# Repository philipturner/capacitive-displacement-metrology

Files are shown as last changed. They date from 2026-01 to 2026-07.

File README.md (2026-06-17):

# Capacitive Displacement Metrology

Phase 0.2/I/II of the [APM Roadmap](https://github.com/philipturner/apm-roadmap)

Objective: Finish a project that has dragged on for 14 months.

Deadline: April 31, 2026 for creepless imaging of graphite

Table of Contents:
- [December 15, 2025](#december-15-2025)
- [December 16, 2025](#december-16-2025)
- [December 18, 2025](#december-18-2025)
- [December 22, 2025](#december-22-2025)
- [January 3, 2026](#january-3-2026)
- [January 5, 2026](#january-5-2026)
- [January 6, 2026](#january-6-2026)
- [January 7, 2026](#january-7-2026)
- [January 8, 2026](#january-8-2026)
- [January 9, 2026](#january-9-2026)
- [January 12, 2026](#january-12-2026)
- [January 13, 2026](#january-13-2026)
- [January 14, 2026](#january-14-2026)
- [January 15, 2026](#january-15-2026)
- [January 16, 2026](#january-16-2026)
- [January 20, 2026](#january-20-2026)
- [January 24, 2026](#january-24-2026)
- [January 26, 2026](#january-26-2026)
- [January 29, 2026](#january-29-2026)
- [January 30, 2026](#january-30-2026)
- [February 2, 2026](#february-2-2026)
- [February 3, 2026](#february-3-2026)
- [February 11, 2026](#february-11-2026)
- [February 12, 2026](#february-12-2026)
- [February 17, 2026](#february-17-2026)
- [February 27, 2026](#february-27-2026)
- [March 8, 2026](#march-8-2026)
- [March 9, 2026](#march-9-2026)
- [March 10, 2026](#march-10-2026)
- [March 12, 2026](#march-12-2026)
- [March 20, 2026](#march-20-2026)
- [March 26, 2026](#march-26-2026)
- [March 28, 2026](#march-28-2026)
- [March 29, 2026](#march-29-2026)
- [April 2, 2026](#april-2-2026)
- [April 27, 2026](#april-27-2026)
- [May 4, 2026](#may-4-2026)
- [Jun 1, 2026](#jun-1-2026)
- [Jun 7, 2026](#jun-7-2026)
- [Jun 17, 2026](#jun-17-2026)

## December 15, 2025

$80,000 worth of wire transfers have hit the bank. I now have enough financial security to proceed with hardware work.

The first step is ensuring I can be paid a full-time salary. Comply with US tax laws, SEC regulations, etc. I predicted the exact numbers before going through the legal boilerplate and setup.

To save effort, serious work <i>probably</i> won't begin until Jan 2 2026. I can avoid filing a few tax return documents for the 2025 year. I will figure out some remaining tax and paperwork stuff during the last days of 2025.

Current estimate for the press release is Dec 18 2025.

## December 16, 2025

This is ridiculous. The United States is the only country where taxes are such a pain: https://www.propublica.org/article/inside-turbotax-20-year-fight-to-stop-americans-from-filing-their-taxes-for-free

## December 18, 2025

I want to make the creepless SPM happen in the shortest amount of time, and publish transparent data that can be fact-checked. To stay true to my motive, I made another attempt to persuade Robert Wolkow to cooperate. I could save many person-hours, recycling existing designs for creepless SPM hardware.

Regardless of whether he shares any design information, I will proceed according to plan. Any data published by other sources should be treated with extreme skepticism. Do not trust any other lab's data, except data gathered in my own house.

| Phase | Description | Voltage |
| ----: | ----------- | ------: |
| 0.2   | PZT metrology | 24&ndash;40 V |
| 1.1   | LiNbO3 metrology | 850 V |
| 1.2   | LiNbO3 kinematic mount | 850 V |
| 2.1   | LiNbO3 STM, graphite sample | 850 V |
| 2.2   | LiNbO3 STM, inverted mode tip registration | 850 V |

I can shortcut to an important milestone, without the expensive vacuum chamber. Just need to speed up the progress with tripod synthesis. No additional employees or contractors needed for hardware design.

At the end of Phase 0.2, we'll reflect on how long this phase took. If it happened quickly, we can reach the end goal with a single employee. Otherwise, I will probably hire a temporary contractor for hardware design. Phase 2.2 should be completed before Dec 31 2026.

> Nomenclature change: exclude Roman numerals from the phase names, at least when numbering sub-phases. It's highly cumbersome to process "I.1" and "II.2", versus "1.1" and "2.2".
>
> In addition, we may right-align the phase names in tables and spreadsheets.

## December 22, 2025

Still figuring out taxes, but making progress. Putting work on the next MNT animation on hold. Not really motivated when the response to the tutorial is anemic.

Figuring out the details of a possible contract with ChimiaDAO. Our funds should last us well beyond 6 months into the future: oversee completion of Phase 0.2, stable income while raising funds for the next round. Progress on the tripod synthesis will be reported in the Phase 0.2 repository, alongside hardware progress.

## January 3, 2026

We are now sufficiently ready to return to experiments. Paid labor will start on January 5. Rippling costs a ridiculous $1,800 sign-on contract over 18 months ($150 down payment). Definitely not what they publicly advertise or what you get from LLM summaries. In the future, we will face similar obfuscation of quotes from hardware suppliers (e.g. UHV-quality turbopumps cost $14,000 minimum).

## January 5, 2026

I will start by resolving an important unknown. How much does it cost to have 500 nm range instead of 80 nm range for the LiNbO3 piezos? This has implications all through Phase III, where we integrate a custom scanner into the vacuum chamber. It explodes the design cost in Phase III because Wolkow will likely be selling his own design. Already designed hardware is cheaper than the person-hours cost of designing new hardware.

https://www.matsusada.com/corporate/management.html

Might contact Matsusada after doing my own research on their products and my performance requirements.

https://www.matsusada.com/column/hvps-safty.html

### Modeling Power Supply Requirements

To be conservative, assume we'll need 3 kinematic mounts for X, Y, and Z. We're also reducing the range, with 6 plates from Wolkow's patent instead of 10. Now all actuators, for all axes, use 6-high piezo stacks. The capacitance of the kinematic mount probably prevents utilization of the PA94 for high slew rates.

Design options for piezo stack geometry:
- 6 plates, 5 mm x 5 mm area, 6 mm stack height
- 6 plates, 10 mm x 10 mm area, 6 mm stack height
- 10 plates, 10 mm x 10 mm area, 10 mm stack height

The plate area is important now, because smaller plates have less capacitance, and thus lower current pulse requirements for the power supply. We may also use different plate areas for the fine vs. coarse actuators. Mechanically, sticking two 5 mm x 5 mm stacks on top of each other would create a 12 mm high tower. Not a good idea.

### Modeling Piezo Force Requirements

To break static friction, the piezo needs to generate a certain amount of force. In addition to the range and waveform frequency requirements.

Assuming a 0.5 mm thick plate and 69.2 GPa shear modulus:

| Voltage | Displacement | Shear Proportion | Shear Pressure |
| ------: | -----------: | ---------------: | -------------: |
| 200 V   | 13.6 nm      | 2.72e-5          | 1.88e6 Pa      |
| 850 V   | 57.8 nm      | 1.16e-4          | 8.00e6 Pa      |

Forces for various setups at 200 V:

| Plate Size | Plate Count | Shear Force | Max Weight |
| ---------- | ----------: | ----------: | ---------: |
| 5 mm x 5 mm   | 1 | 47.1 N | 4.8 kg |
| 5 mm x 5 mm   | 3 | 141.1 N | 14.4 kg |
| 10 mm x 10 mm | 1 | 188.2 N | 19.2 kg |
| 10 mm x 10 mm | 3 | 564.7 N | 57.6 kg |

Forces for various setups at 850 V:

| Plate Size | Plate Count | Shear Force |
| ---------- | ----------: | ----------: |
| 5 mm x 5 mm   | 1 | 200.0 N | 20.4 kg |
| 5 mm x 5 mm   | 3 | 600.0 N | 61.2 kg |
| 10 mm x 10 mm | 1 | 800.0 N | 81.6 kg |
| 10 mm x 10 mm | 3 | 2399.9 N | 244.9 kg |

Even though shear force doesn't increase with the number of plates per stack, the above numbers should exceed all reasonable force requirements.

### Modeling Required Slew Rate

Dive deeper into the waveform requirements for stick-slip nanopositioning:
- Does the waveform need to contain components above the resonance frequency?
- What is the target rate in steps/second?
- Why is woodpecker coarse tip approach so slow?

These variables can probably be resolved at a later date. I mostly want a lower capacitance in the kinematic mount, while still attaining 30 V/μs slew rate of the PA95 op amp.

### Design Space Exploration

Quiescent current demands on power supply:
- Conservatively 6 DAC channels and 6 PA95 op amps for Phase III
- 6 * 2.2 mA = 13.2 mA

Capacitance (in pF) of entire kinematic mount:
- Piezo plate count is 18 (3 stacks, each with 6 plates)
- Dielectric constant of lithium niobate at 300 K is 88
- Thickness of each plate is 0.5 mm

| Configuration | Capacitance |
| ------------- | ----------: |
| 5 mm x 5 mm   | 701         |
| 10 mm x 10 mm | 2805        |

Current (in mA) required to drive the kinematic mount:

| Configuration | 30 V/μs | 20 V/μs | 10 V/μs | 5 V/μs | 3 V/μs |
| ------------- | ------: | ------: | ------: | -----: | -----: |
| 5 mm x 5 mm   | 21.0    | 14.0    | 7.0     | 3.5    | 2.1    |
| 10 mm x 10 mm | 84.2    | 56.1    | 28.1    | 14.0   | 8.4    |

Power (in W) generated by either of the 450 V power supplies:
- Each supply operates at ~50% duty cycle
- Each supply operates during the respective edge of the waveform
  - +450 V for rising
  - -450 V for falling

| Configuration | 30 V/μs | 20 V/μs | 10 V/μs | 5 V/μs | 3 V/μs |
| ------------- | ------: | ------: | ------: | -----: | -----: |
| 5 mm x 5 mm   | 9.5     | 6.3     | 3.2     | 1.6    | 0.9    |
| 10 mm x 10 mm | 37.9    | 25.2    | 12.6    | 6.3    | 3.8    |

Frequency of an 850 V triangle wave:

| Slew rate (V/μs)     | 30   | 20   | 10  | 5   | 3   |
| -------------------- | ---: | ---: | --: | --: | --: |
| Rise time (μs)       | 28   | 43   | 85  | 170 | 283 |
| Wave period (μs)     | 57   | 85   | 170 | 340 | 567 |
| Wave frequency (kHz) | 17.6 | 11.8 | 5.9 | 2.9 | 1.8 |

### Final Current Demands

Making the smart design choice to use 5 mm instead of 10 mm piezo plates for the kinematic mount.

Providing two negotiable options for maximum waveform frequency: 5.9 kHz, 17.6 kHz

| Wave frequency                        | 5.9 kHz  | 17.6 kHz |
| ------------------------------------- | -------: | -------: |
| Quiescent current                     | 13.2 mA  | 13.2 mA  |
| Current of one active kinematic mount |  7.0 mA  | 21.0 mA  |
| Peak current in either 450 V supply   | 20.2 mA  | 34.2 mA  |
| Peak power in either 450 V supply     | 9.1 W    | 15.4 W   |
| Average power in either 450 V supply  | 7.5 W    | 10.7 W   |
| Total power in both supplies combined | 15.0 W   | 21.3 W   |

I will state the peak (not average) demands when emailing Matsusada.

## January 6, 2026

Still waiting to hear back. Customer service things tend to take a long time, and have many delays.

Where else can I make progress regarding the pathway to a final-state LiNbO3 SPM? The design of a custom UHV chamber with custom electrical feedthroughs. Not the UHV-SPM system that Wolkow might be selling.

### Sample Preparation Concerns

Monocrystalline Au(111) surfaces are indeed very expensive. Most vendors obfuscate the prices. I recall one vendor on Google Search showing $2,400. Several months ago, I remember a different vendor saying $3,000 publicly. There's a research paper about reducing the cost of Au(111) surface production: https://pubs.acs.org/doi/full/10.1021/acsnano.4c17431

I will start with trying to reproduce Dan Berard's results, with my imperfect Au(111) "textured" surface prepared at Virginia Tech. Next, reproduce the self-assembled monolayer structure of densely packed tripods on gold. If everything works well, attempt a sparse monolayer that can generate reverse-phase images (RPIs) from the CBN paper.

I'm highly skeptical this will work out. We may need complicated EC-STM or $3,000 pristine commercial gold samples. However, both of these are cheaper/better than a complete UHV chamber.

The end state of this sample preparation must be something actually usable for inverted mode mechanosynthesis.

---

<b>Second concern:</b> do we need to bake off the Au surface prior to entering into the UHV chamber? That would remove all the tripods deposited in solution. I want to avoid the vapor-phase deposition of tripods onto gold, that previous literature used.

<b>Worst case:</b> final vacuum system requires complicated and expensive MBE and/or XPS hardware. But the chemical design space for Au-S linkers is still unlocked.

---

Other important preliminary tasks to remember:
- What is going on with the crystallographic vectors and shear directions for 41 X-cut lithium niobate?
  - Does some extra displacement happen in the off-axis direction?
  - What is the physical (atomic) justification for perfect 90 degree misalignment between E-field and position displacement?
  - Lithium niobate is symmetric, so there should be multiple directions where such a coupling occurs.
  - Might use [Molecular Renderer](https://github.com/philipturner/molecular-renderer) to visualize crystal atoms and control programmable animations.
- Why is coarse tip approach so slow?

### Update

Got the first email response back from Matsusada. Working on the next steps regarding our discussion.

Regarding electrical feedthroughs for vacuum systems: it boils down to dielectric breakdown and [Paschen's curve](https://en.wikipedia.org/wiki/Paschen%27s_law#/media/File:Paschen_curves.svg). I don't think I need to spend much additional time on this topic, for now.

I'll call it a day for now. Tomorrow, I will investigate the crystallographic vectors of lithium niobate.

## January 7, 2026

The Islam and Beamish (2018) precursor paper corrects for the effect of the 41° angle on the piezo constant. They measured a 23 ppm change in capacitance at 300 μm. Voltage was 40 V and there were 3 plates in the stack. Raw data for piezo constant should be 57.5 pm/V, but they stated 49.7 pm/V in the paper. I reproduced the ratio of 57.5 vs 49.7 when simulating the response of 41° vs 0° cut lithium niobate.

I think positive 41° means the manufacturer rotated the crystal boule by that amount. The reference plane ready to slice a wafer hasn't moved. This explains why the script has to invert the rotation angle to match literature data.

Wafers from Crystal Substrates have no special 41° rotation. They are xyt 0° in IRE notation. Provided that you select "X-cut (1 1 2-bar 0)".

Lithium Niobate Orientation

---

[PiezoelectricCoefficients2.swift](./Code/Simulation/PiezoelectricCoefficients2.swift)

The actual shear constant is 80 pm/V, in a direction 32° counterclockwise from Z (0 0 0 1). The electric field is always being applied across the X-axis, regardless of the rotation of the wafer cut. If Wolkow has realized this, then the 80 nm quoted from the patent corresponds to 167 V at 6 piezo plates. Not 196 V.

```
swift PiezoelectricCoefficients2.swift 0

// 0°
//  ∂(∂u/∂x1)/∂E1: SIMD3<Float>(0.0, -21.0, 34.0) pm/V
//  ∂(∂u/∂x2)/∂E1: SIMD3<Float>(-21.0, 0.0, 0.0) pm/V
//  ∂(∂u/∂x3)/∂E1: SIMD3<Float>(34.0, 0.0, 0.0) pm/V

// 0°
//  u (x-axis): [0.0, -17.9, 28.9] nm
//  u (y-axis): [-178.5, 0.0, 0.0] nm
//  u (z-axis): [289.0, 0.0, 0.0] nm

// 0°
//  u (x-axis): [0.0, -35.7, 57.8] nm
//  u (y-axis): [0.0, 0.0, 0.0] nm
//  u (z-axis): [0.0, 0.0, 0.0] nm
```

```
swift PiezoelectricCoefficients2.swift 32

// 32°
//  ∂(∂u/∂x1)/∂E1: SIMD3<Float>(0.0, 0.20824544, 39.961945) pm/V
//  ∂(∂u/∂x2)/∂E1: SIMD3<Float>(0.20824254, 0.0, 0.0) pm/V
//  ∂(∂u/∂x3)/∂E1: SIMD3<Float>(39.961945, 0.0, 0.0) pm/V

// 32°
//  u (x-axis): [0.0, 0.2, 34.0] nm
//  u (y-axis): [1.8, 0.0, 0.0] nm
//  u (z-axis): [339.7, 0.0, 0.0] nm

// 32°
//  u (x-axis): [0.0, 0.4, 67.9] nm
//  u (y-axis): [0.0, 0.0, 0.0] nm
//  u (z-axis): [0.0, 0.0, 0.0] nm
```

```
swift PiezoelectricCoefficients2.swift 41

// 41°
//  ∂(∂u/∂x1)/∂E1: SIMD3<Float>(0.0, 6.4571033, 39.437363) pm/V
//  ∂(∂u/∂x2)/∂E1: SIMD3<Float>(6.4571033, 0.0, 0.0) pm/V
//  ∂(∂u/∂x3)/∂E1: SIMD3<Float>(39.437366, 0.0, 0.0) pm/V

// 41°
//  u (x-axis): [0.0, 5.5, 33.5] nm
//  u (y-axis): [54.9, 0.0, 0.0] nm
//  u (z-axis): [335.2, 0.0, 0.0] nm

// 41°
//  u (x-axis): [0.0, 11.0, 67.0] nm
//  u (y-axis): [0.0, 0.0, 0.0] nm
//  u (z-axis): [0.0, 0.0, 0.0] nm
```

If we double the plate Y and Z dimensions to 10 mm, the 41 degree case changes from 54.9 to 109.8 nm, and from 335.2 to 670.4 nm. But after correcting for the ratio of X dimension to Y or Z dimension and summing into the X-axis shear, the true displacement is still 11.0 nm and 67.0 nm.

---

The X axis of the crystal boule doesn't create any charge when compressed. It cannot, because the crystal structure is symmetric across the YZ plane. The Y and Z axes in IRE notation are piezoelectric. That explains why they produce displacements.

I can imagine 6 symmetry operations for a valid pair of E-field axis and shear direction. The shear piezo constant is 80 pm/V, not 68 pm/V.

| X, Y, Z Principal Axes | Shear Direction |
| ---------------------- | -----------: |
| standard IRE orientation                       | Z rotated +32° counterclockwise about X |
| rotate X, Y by  +60° counterclockwise around Z | Z rotated -32° counterclockwise about X |
| rotate X, Y by +120° counterclockwise around Z | Z rotated +32° counterclockwise about X |
| rotate X, Y by +180° counterclockwise around Z | Z rotated -32° counterclockwise about X |
| rotate X, Y by +240° counterclockwise around Z | Z rotated +32° counterclockwise about X |
| rotate X, Y by +300° counterclockwise around Z | Z rotated -32° counterclockwise about X |

Due to the IRE standard, readily stocked commercial wafers only fall in the first row. But in theory, there are 5 other crystal cuts with the same piezoelectric response. Rows 3 and 5 are equivalent to row 1 by a symmetry operation. Thus, the IRE standard has prevented the opposite chirality of X-cut lithium niobate (rows 2, 4, 6) from ever reaching the market.

In Islam and Beamish (2018), the erroneous off-axis displacement would not be measured. Moving the parallel plates in a direction parallel to each other, will decrease the capacitance no matter which direction it moves. The case of zero off-axis displacement is a local maximum of capacitance. The first derivative with respect to position is zero. In contrast, the first derivative with respect to on-axis displacement (distance between the two plates) is very high. It is the only component that could affect the measurements.

## January 8, 2026

I did some investigation of why coarse tip approach is slow. There are three limiting factors:
- Allowed positional excursion before tip crashes, relative to point of minimum detectable current
- Delay for sensor to register the tip's new position
- Inertial overshoot even after the piezo stops applying force

At the speeds we're moving, capacitive currents have no effect on measurements.

| Bias Voltage | dC/dx | dx/dt | Capacitive Current |
| -----------: | ----: | ----: | -----------------: |
| 1 V          | 1.50e-10 F/m | 5.88 μm/s | 0.9 fA |
| 3 V          | 1.50e-10 F/m | 5.88 μm/s | 2.6 fA |

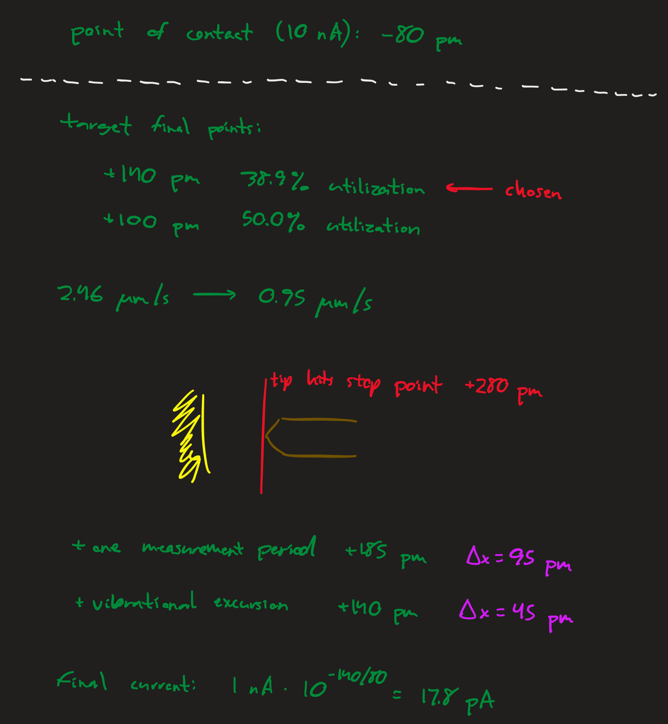
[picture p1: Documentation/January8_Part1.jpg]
January 8, Part 1


The allowed positional excursion was set to 280 pm, the difference between 1 nA and 313 fA at 80 pm/decade. True tip crash likely occurs at 10 nA, or a limit of 360 pm. To improve the safety margin, the target displacement is half of the 280 pm range, or 140 pm.

Next, the delay of the sensor. Although Dan Berard and similar STMs may have an ADC bandwidth of 200 kHz, the limiter is the ~10 kHz pole of the 100 MΩ TIA design. I also conservatively derated the ADS8699 from 15 kHz to 10 kHz. The limiter here is not digitization frequency, but rather the analog response latency from the lowpass filter.

If we model the delay as limitations on sinewave frequency, we get 10 kHz. That was used for calculations in the screenshot above. If we model it as exponential decay with a time constant of RC, we only need 2 or 3 time constants (settling to 13.5% or 5.0%), not 2π time constants. I'll correct for this in a bit.

Finally, the vibrational excursion. This is easier to model than I anticipated. The velocity is the angular frequency at resonance, times the positional amplitude of the vibration. I used [3340 Hz](https://github.com/philipturner/transimpedance-amplifier?tab=readme-ov-file#september-9-2025) eigenfrequency from FEM simulations, which is better than most STMs.

In the screenshot above, the maximum acceptable velocity was 0.95 μm/s.

### Correction for more optimistic sensor response time

| RC Time Constants | Sensor Error from Lag | Proportion of Limit from Vibrational Excursion | Maximum Acceptable Velocity |
| ----------------: | --------------------: | ---------------------------------------------: | --------------------------: |
| 6.28              | 0.2%                  | 32.1% | 0.95 μm/s |
| 3.00              | 5.0%                  | 49.8% | 1.47 μm/s |
| 2.00              | 13.5%                 | 59.8% | 1.77 μm/s |
| 1.00              | 36.7%                 | 74.9% | 2.21 μm/s |

Anything shorter than 3 RC time constants seems questionable. I'll set the revised velocity to 1.47 μm/s.

---

Next, walk through the algorithm for coarse displacements during tip approach.

Start with a conservatively slow waveform. The time to move the tip during the coarse steps is a tiny fraction of the overall time during coarse approach. Start with a 1 kHz triangle wave, 850 V peak-to-peak amplitude, or ±425 V. Displacement range is 408 nm, or ±204 nm. Each edge of the wave form takes 500 μs. Slew rate is 1.7 V/μs, much less than the PA95's limit of 30 V/μs. Speed is 816 μm/s. The kinematic mount moves back and forth at 816 μm/s in alternating directions, always returning to the same position.

| Kinematic Mount | Mass of Load | Equivalent Gravitational Force | Force in Pounds |
| --------------- | -----------: | -----------------------------: | --------------: |
| X Axis          | 13.02 g      | 127.6 mN | 0.03 lb |
| Y Axis          | 23.37 g      | 229.0 mN | 0.05 lb |
| Z Axis          | 8.94 g       | 87.6 mN  | 0.02 lb |

---

Using the N42 grade of magnets.

Magnets need to be extremely close to the surface, to achieve optimal force. I'm setting 300 μm tolerance as the practical upper limit, which nerfs magnetic force ~50% for my geometry. The smaller X and Z kinematic mount can use two 5 mm magnets, while the Y kinematic mount can use four.

Playing around with parameters on: https://www.kjmagnetics.com/magnet-strength-calculator.asp?srsltid=AfmBOorsJBupnrQ9hcxNIcvuajbopfTptJDigBCl6Y_YctyCHKSyzlxy

| Diameter | Thickness | Distance | Pull Force Case 1 |
| -------: | --------: | -------: | ----------------: |
| 5 mm     | 3 mm      | 0.0 mm   | 1.45 lb           |
| 5 mm     | 5 mm      | 0.0 mm   | 2.04 lb           |
| 5 mm     | 7 mm      | 0.0 mm   | 2.19 lb           |
| 10 mm    | 3 mm      | 0.0 mm   | 4.33 lb           |
| 10 mm    | 5 mm      | 0.0 mm   | 6.48 lb           |
| 10 mm    | 7 mm      | 0.0 mm   | 7.73 lb           |

| Diameter | Thickness | Distance | Pull Force Case 1 |
| -------: | --------: | -------: | ----------------: |
| 5 mm     | 3 mm      | 0.3 mm   | 0.73 lb           |
| 5 mm     | 5 mm      | 0.3 mm   | 1.05 lb           |
| 5 mm     | 7 mm      | 0.3 mm   | 1.15 lb           |
| 10 mm    | 3 mm      | 0.3 mm   | 2.75 lb           |
| 10 mm    | 5 mm      | 0.3 mm   | 4.19 lb           |
| 10 mm    | 7 mm      | 0.3 mm   | 5.07 lb           |

| Diameter | Thickness | Distance | Pull Force Case 1 |
| -------: | --------: | -------: | ----------------: |
| 5 mm     | 3 mm      | 1.0 mm   | 0.29 lb           |
| 5 mm     | 5 mm      | 1.0 mm   | 0.44 lb           |
| 5 mm     | 7 mm      | 1.0 mm   | 0.50 lb           |
| 10 mm    | 3 mm      | 1.0 mm   | 1.50 lb           |
| 10 mm    | 5 mm      | 1.0 mm   | 2.36 lb           |
| 10 mm    | 7 mm      | 1.0 mm   | 2.90 lb           |

We do need two magnets aligned in the center of the path of motion. Both Voigtlander and Wolkow's reference designs do this. We can just tweak the force for the Y-axis magnets to be doubled.

All numbers in the above tables are an order of magnitude greater than the amount required to counteract gravity. I will use a design where all kinematic mounts are 45° away from perfectly vertical, and the Y axis's direction of motion is perpendicular to gravity. That does not remove the disparity in load mass between kinematic mounts; it just seems like the most sensible geometry.

To start, let's set the magnet force to 0.50 lb (2.22 N) for all kinematic mounts. This is probably too large, but we can correct it later if needed. In addition, the coefficient of static friction is 0.5 and the coefficient of kinetic friction is either 0.3 or 0.4. We want to explore a combinatorial space for uncertainty in the nature of friction. Finally, the transition from stationary to the "riding" part of the waveform is smoothed out enough to not break static friction. The computer code controlling the DAC makes this part of the waveform smooth.

---

Another interesting observation is the disparity between resonance frequencies relevant to this analysis, and resonant frequency of the tip-sample mechanical loop (3340 Hz). We are localizing the analysis to the kinematic mount subsystem, which is much stiffer and spatially smaller than the whole STM. In addition, we are not examining any possible mode (the floppiest mode), but the direction of vibration parallel to motion. What we need to worry about regarding minimum eigenfrequencies, is coupling to other floppier modes and exciting them. We prevent this by only repeating the sawtooth waveform at a 1 kHz frequency. Thus, extremely high frequencies of ~50 kHz could define settling times for stick-slip action.

Shear stiffness of three 5 mm x 5 mm stacks: 600 N / 408.0 nm = 1.47 GN/m. If the stacks were 10 mm x 10 mm, the stiffness would increase fourfold and frequency would increase twofold.

| Kinematic Mount | Mass of Load | Stiffness | Frequency |
| --------------- | -----------: | --------: | --------: |
| X Axis          | 13.02 g      | 1.47 GN/m | 53500 Hz  |
| Y Axis          | 23.37 g      | 1.47 GN/m | 39900 Hz  |
| Z Axis          | 8.94 g       | 1.47 GN/m | 64500 Hz  |

Another note: since our range is a conservatively large 408 nm, we don't need to worry about extremely small displacements (80 nm) on the border of impossible to break the covalent bonds for static friction. It is now much easier to model the behavior of stick-slip action.

I'll try a sophisticated time-stepping simulation in a Swift script, with a time step of 1 microsecond. For reference, at the maximum slew rate of 30 V/μs, it takes 28 microseconds to complete the voltage ramp. By sophisticated, I mean it includes all relevant variables and calculates the kinematic equations. The integrator will be a simple Euler algorithm. Trajectory shapes will be visualized in the console, rather than a fancy graph. Although the time stepping resolution is 1 microsecond for accuracy, resolution of data presentation will be more like 5 microseconds. All numbers will be in FP32 because we don't need FP64.

At high frequency, the piezo doesn't move instantly in response to voltage. An instantaneous force of O(600 N) is generated. Then, within the resonant period of O(20 μs), the piezo moves to the expected position. There is no high-frequency creep that would lead to hysteresis. The simulation will show a growing force calculated from the difference between the piezo's actual and desired position, as set by the control voltage. The force will eventually push the piezo to the desired position, and it will overshoot (resonance), oscillating around the desired point. We should test that, in a basic form of the simulation, the oscillation never dies out because there is no damping/friction.

<b>First doable goal:</b> set up a simulation that reproduces the behavior in the above paragraph.

---

After reflecting on [this physics page](http://hyperphysics.phy-astr.gsu.edu/hbase/frict2.html), I should expand the combinatorial space for coefficient of kinetic friction. Now include 0.3, 0.4, and 0.5. There is an asymmetry between static and kinetic friction purely due to the shape of the graph.

Once the simulation is debugged and investigated, I can export CSV to plot on Google Sheets and present here. If that is needed.

I will just examine the Z kinematic mount for this analysis. Although it represents the far end of the distribution of load masses, it is a sane way to reduce the size of the combinatorial space. Compared to examining two or three kinematic mounts. I will also change so, instead of pointing at a 45-degree angle, gravity points directly parallel to the direction of motion. This choice simplifies the code.

## January 9, 2026

I just sorted out a few more interesting details about how to simulate kinetic friction. I will incorporate the notes into the Swift script.

[StickSlipAction.swift](./Code/Simulation/StickSlipAction.swift)

I have reproduced the piezoelectric vibration quite intricately. The first doable goal is completed. I added viscoelastic damping and smoothed out the control voltage waveforms, slightly reducing the amount of vibrational energy.

Task 2: add kinetic friction

<s>Task 3: add gravity and vary the magnet's strength</s>

[StickSlipAction2.swift](./Code/Simulation/StickSlipAction2.swift)

The script has improved significantly. I plan on investigating gravity &times; magnet force, after studying coefficient of kinetic friction &times; kinetic velocity threshold &times; slew rate.

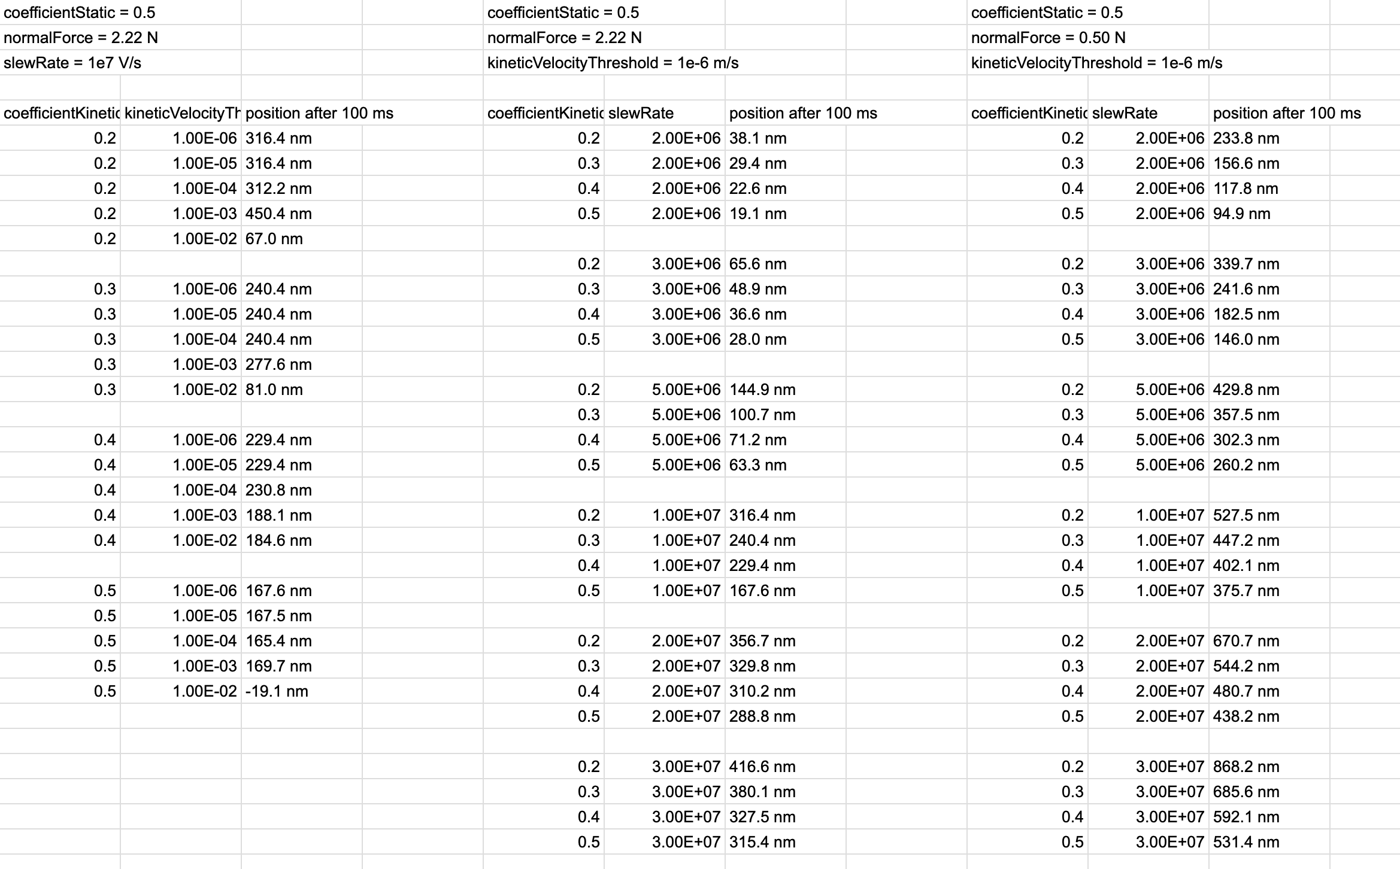
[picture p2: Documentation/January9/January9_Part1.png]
January 9, Part 1


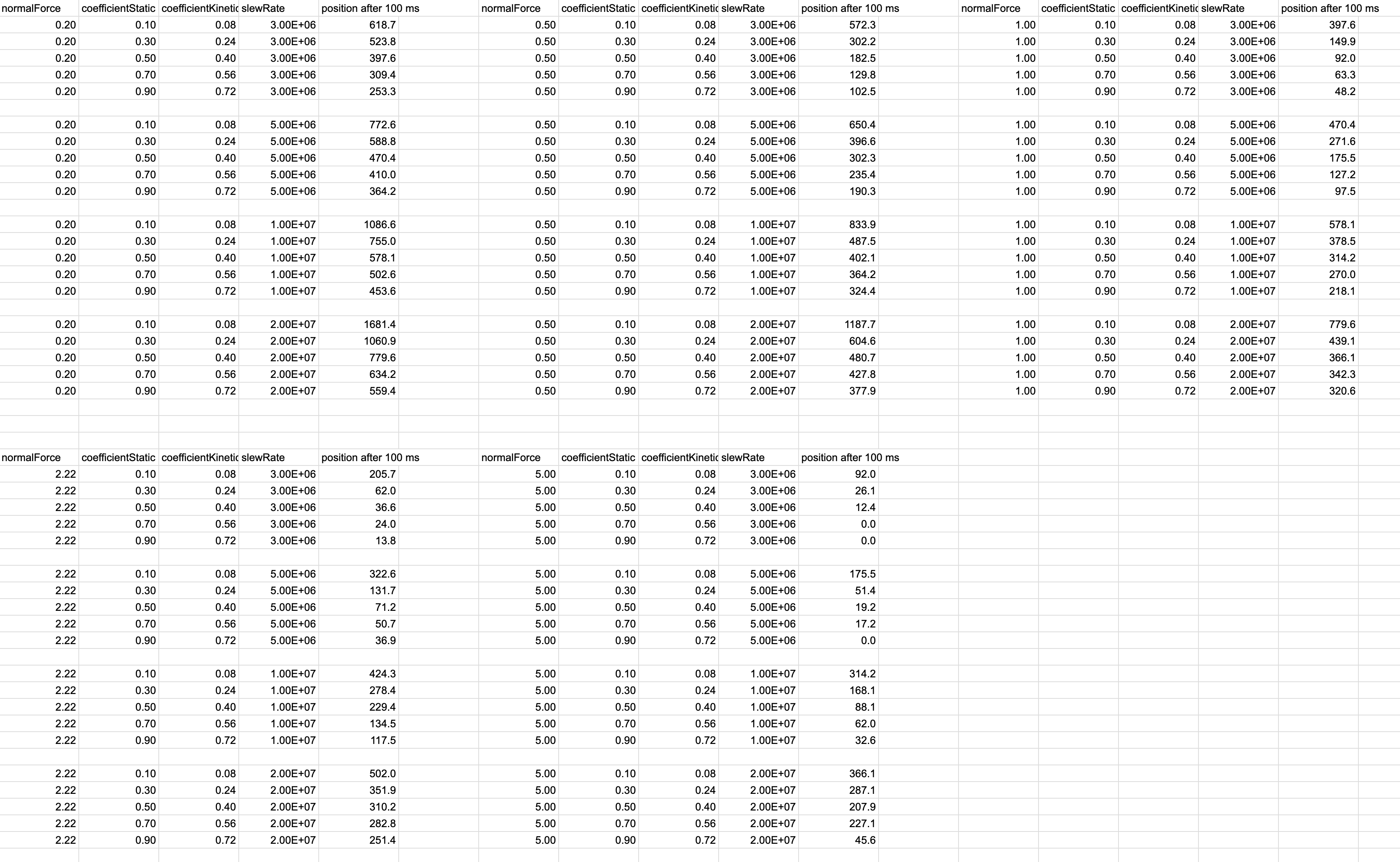
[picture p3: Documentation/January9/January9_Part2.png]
January 9, Part 2


I still plan to study the effect of gravity, and using stronger magnets to prevent bad outcomes. I have the time budget to do due diligence here.

## January 12, 2026

I found an error in the script. Instead of the piezo stiffness being 1.47 GN/m, it should be 1.73 GN/m. The problem stems from taking 600 N / 408 nm, when the two inputs to this division are incorrect. The piezo constant has changed from 68 pm/V to 80 pm/V. Either take 705 N / 408 nm or 600 N / 347 nm.

Regarding stiffness: shear modulus is set to 69.2 GPa. Copper plates and epoxy could make the piezo more compliant. Copper has 2/3 the Young's modulus of LiNbO3 and consumes ~50% of the stack's volume. Epoxy is 3 GPa and consumes 10% or less of the volume. Before derating the stiffness by 50%, I need to work through the piezoelectric constitutive equations and understand the effects.

I think we can neglect the effects of epoxy on stiffness. A non-negligible layer would derate the stiffness by a factor of up to 10. In the literature, a resonance frequency of 171 kHz matched bulk moduli of LiNbO3 and Cu after dividing the frequency by 2. Alternatively, the questionable "electromechanical transformer ratio" of 0.15 N/V reflected stiffness derating of epoxy consuming 5% of total volume.

| Model | Stiffness, 1 Plate | Stiffness, 6 Plates | Stiffness, 3 Stacks |
| ----- | -----------------: | ------------------: | ------------------: |
| single LiNbO3 plate (0.5 mm)  | 3.462 | 0.577 | 1.731 |
| plate + Cu electrode (0.5 mm) | 1.288 | 0.215 | 0.644 |
| above + epoxy layer (0.05 mm) | 0.388 | 0.065 | 0.194 |

_All table entries are in GN/m._

| Model | Stiffness, 6 Plates | Resonance @ 1.02 g |
| ----- | ------------------: | -----------------: |
| single LiNbO3 plate (0.5 mm)  | 0.577 GN/m | 119.7 kHz |
| plate + Cu electrode (0.5 mm) | 0.215 GN/m |  73.1 kHz |
| above + epoxy layer (0.05 mm) | 0.065 GN/m |  40.2 kHz |

I need to revise the kinematic mount's stiffness to 0.644 GN/m. Compared to yesterday's data, vibrational responses should be 1.5x slower.

For the piezoelectric constitutive equations, shear modulus (c<sup>E</sup>) should change from 69.2 GPa to 25.7 GPa.

---

I have now documented the entire combinatorial space of variables for a kinematic mount:
- Different axes (X, Y, Z) having different masses
- Coefficient of static and kinetic friction, not necessarily being proportional to each other
- Various slew rates up to the limit of 30 V/μs
- Gravity acting toward, against, or perpendicular to stepping direction
- Magnet strength varying from 0.1 N (0.02 lb) to 5.6 N (1.26 lb), on a logarithmic scale with 1.4x steps

[LiNbO3 Piezo Calculations (Google Sheets)](https://docs.google.com/spreadsheets/d/1vBnCa-WxlORrH1MnVM8QzBGzUekIoL9DoZVunZ4Nscg/edit?gid=2067282552#gid=2067282552)

The Google Sheet covers 1.65 thousand permutations of the ~5 controlling variables. Next, I will study the data and make sense of it. If possible, draw conclusions that help with IRL design specification.

### Insights

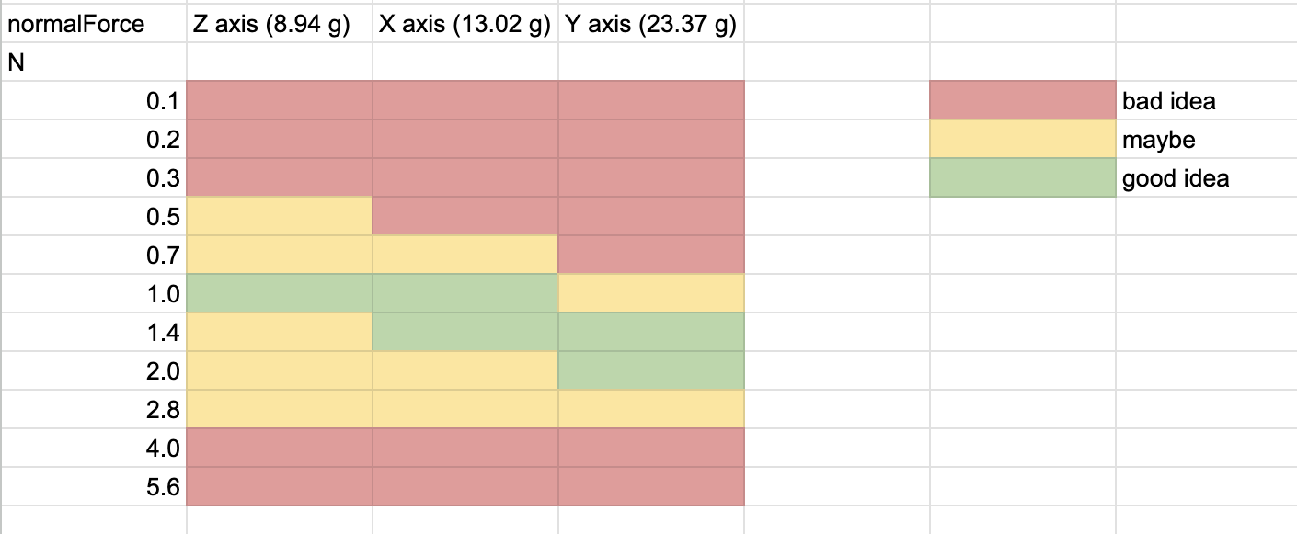
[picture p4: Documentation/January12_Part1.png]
January 12, Part 1


I will likely need to test a few permutations of the design IRL, to calibrate the right magnet force. Also, be cautious about magnets demagnetizing in UHV during bakeout.

I can also run FEM simulations with Elmer in FreeCAD. Use [FEM EquationMagnetodynamic](https://wiki.freecad.org/FEM_EquationMagnetodynamic) and calculate nodal forces. Also, valuable statement from the FreeCAD docs:

> Despite the name, the Magnetodynamic equation can be used to perform magnetostatic analyses.

## January 13, 2026

I now need to embark on a difficult task: specify the core mechanical layout of the metrology junction. But before that, I would like to read up more on epoxy. Specify how LiNbO3 piezo stacks would be fabricated.

A couple of questions (but not all):
- What temperature is epoxy baked at?
- Are rough or smooth substrate surfaces best for applying epoxy?
- How much does UHV-quality epoxy cost?

---

24 V * 80 pm/V * 6 = 11.52 nm

I could speed up progress by ordering the AH2550 now, and testing the first LiNbO3 piezo stack with low voltage. The metrology junction should be capable of both shear and longitudinal piezo types. Alternatively, ThorLabs sells [single shear piezos](https://www.thorlabs.com/low-voltage-shear-piezoelectric-chips-and-stacks) for \~$90. This cost pales in comparison to the AH2550 (\~$1,000).

This product has the same physical dimensions as a 5 mm x 5 mm x 0.5 mm LiNbO3 piezo plate. It has a piezo constant of 2.00&ndash;3.25 nm/V, depending on hysteresis and creep. Compare that to a stack of six LiNbO3 plates, at 0.48 nm/V.

Two derisking notes:
- Consider buying an extra pack of ten 5 mm x 5 mm plates from Crystal Substrates. If the experiment with 6 plates fails, I will barely have any backup. And the 3 week lead time is concerning. Alternatively, use 4 plates (just 7.68 nm displacement) for this experiment.
- To do due diligence in saving time, ask whether ThorLabs could contract out the labor and equipment for bonding plates with epoxy. If their lead times are as ridiculous as Boston Piezo Optics (6&ndash;8 weeks), fabricate the piezo stacks in-house.

Jumping directly to using AH2550, instead of designing a PCB with AD7745, will save much time. Another time saver is trying the DAC81401 with hand-soldering, just higher tip temperatures this time. Design the circuit to easily swap in up to 10 trial boards for the DAC. No need for the complexity of solder paste and reflow ovens yet.

Perhaps, with the type of displacements involved, we don't even need the DAC. Just a battery with a multimeter checking the exact voltage. But we are building hardware infrastructure for the kinematic mount in Phase I and II. That will require programmable, controlled waveforms amplifying the DAC8140x output to the PA95. It's better to not cut corners, and to also fix the problems causing DAC failure in Phase 0.1.

| Function | Cheap Option | Expensive Option |
| -------- | ------------ | ---------------- |
| power supply | 9V batteries, ±18&ndash;22 V regulators | Matsusada ±650 V power solution |
| DAC      | DAC81401, ±12&ndash;20 V | PA95, amplify ±20 V to ±425 V |
| ADC      | ADS8699        | oscilloscope |
| capacitance sensor | AD7745 | AH2550 |

_By switching to the expensive options, the number of TSSOPs on a custom PCB is reduced. That reduces the need for reflow soldering, and reduces design cost of PCB layout._

24 V regulators may be a more expensive product grade than 18 V regulators. The DAC81401 cannot operate with 48 V across its power terminals; only 44 V absolute maximum, 43 V recommended. In the Art of Electronics, one possibility is adjustable regulators like LM317, except rated for higher voltage.

Another option is, in the final design, amplify ±12 V to ±425 V. That would be a gain factor of 35.4 instead of 21.3. The example circuit on the PA95 datasheet has 100x gain and a 10 pF compensation capacitor. With a 4.7 pF capacitor, the gain-bandwidth tradeoff sets a maximum bandwidth of 100 kHz at 100x gain. But this curve is just for small signals and calculating loop stability. At large signals, a 4.7 pF capacitor limits the frequency to 15 kHz for 850 Vpp swings.

I think there is enough product selection, as least for adjustable LM317-style regulators, to have 36 V input and 21.5 V output of both polarities. At least for this experiment in the low-voltage regime, I would prefer ±20 V instead of ±12 V. Maximum piezo stacks should be 4 plates, at least for now because of limited stock. In the future, a full kinematic mount and multiple fine axes will require more orders from Crystal Substrates. At that point, I will consider 6 plates to maximize range.

| Actuator | Piezo Constant | Range |
| -------- | -------------: | ----: |
| ThorLabs shear plate | 2.00 nm/V | 80.0 nm |
| single LiNbO3 plate | 0.08 nm/V | 3.2 nm |
| four LiNbO3 plates | 0.32 nm/V | 12.8 nm |

_Displacements of various actuators accessible with 40 Vpp and existing stock of LiNbO3 plates. In the Islam and Beamish papers, sensor resolution was 0.1 nm with 4 seconds of averaging time._

---

I just got some leads on lower-cost alternatives to $2500 and $3000 costs for pristine (not "textured") Au(111) samples. I will need to question the suppliers and ensure they actually did the annealing step after sputtering.
- [Arrandee - $139.79](https://www.arrandee.com)
- [MSE Supplies - $299.95](https://www.msesupplies.com/products/platypus-high-quality-gold-au-thin-films-on-substrates)
- [Ted Pella - $147.40](https://www.tedpella.com/vacuum_html/Substrates_Supports_Wafers_Slides.aspx#_16012_G)

I'm still trying to stay on good terms with Wolkow. It's just, all the economic motivations require that I act in my own interests. I wish him the best of luck in proliferating creepless SPMs, but his products have insufficient specifications for my research. That's why I need an open source design.

## January 14, 2026

Today's discoveries:
- Use a Controleo3 reflow oven to cure the epoxy at 120°C
- Best if a compact 3D-printed or similar isolator is used, rather than a bulky table like the OpenSTM design. Keep the same height dimension, just shrink the lateral dimensions.
- By averaging several samples each at 9.1 Hz, it might be possible to vastly surpass the ~25 aF six-sigma noise of the AD7745

## January 15, 2026

Instead of 9V batteries, I should try sourcing the ±21.5 V and ±15 V linear regulators from a commercial "power box". The box(es) rely on residential AC power and output a bipolar ±30 V. Through a chain of low-voltage regulators, this box also supplies +5 V and +3.3 V for digital circuitry in the data converters. Altogether, the power module should not cost more than $100. I would like it to be cheap.

To run the DAC81404 at ±20 V output, tolerance from the linear regulator is razor thin. Recommended maximum and amount of power supply footroom is 1.5 V. Absolute maximum is 2.0 V. I will need to run the math on tolerances for LM337-style regulators. Even 2% off from 21.5 is 21.0 or 22.0. The reference voltage of the LM337 can vary ±4%. We will need trimming potentiometers.

It looks much simpler to take the range reduction of ±20 V -> ±12 V. The plan is to recycle this one PCB for Phase 0.2, I, and II. In later phases, we only need ±12 V for bias voltage, and the increased gain of 20x -> 35x for PA95 is acceptable. Design cost and usability issues are lower, if a single ±15 V regulator supplies both the DAC and TIA. Even if a separate regulator supplies the DAC vs. TIA, the advantage is clear.

---

Phase 0.2 hinges on using averaging over multiple data samples, to drastically improve the resolution of the AD7745. Here are the multiplicative factors:
- Taking ~100 samples at ~10 Hz, reduce 6σ noise from 25.5 aF to 2.67 aF. Compare that to 1.3 aF from the Islam and Beamish paper, and the 0.8 aF limit for AH2550A. <b>10.0x</b>
- One vs. four LiNbO3 plates: <b>4.0x</b>
- 24 V vs. 40 V range: <b>1.67x</b>
- Orienting plates along the 32° shear direction: <b>1.17x</b>

Let's examine this, starting with a single LiNbO3 plate, not aligned at any angle, and no improvements stated above. 68 pm/V * 24 V = <b>1.63 nm</b>. 25.5 aF * (1 nm / 13 aF) = <b>1.96 nm</b>.

Now, just examine the improvement from averaging 100 samples for 10.0 seconds. 2.67 aF * (1 nm / 13 aF) = <b>0.21 nm</b>. The displacement is now vastly within resolution of the sensor.

Instead, consider only improving the state of a single LiNbO3 plate. 80 pm/V * 40 V = <b>3.20 nm</b>.

Finally, consider only changing the number of plates. 4 * 68 pm/V * 24 V = <b>6.53 nm</b>.

|               | Piezo Range | Sensor Noise Envelope |
| ------------- | ----------: | --------------------: |
| Original      | 1.63 nm     | 1.96 nm               |
| Improvement 1 | 1.63 nm     | 0.21 nm               |
| Improvement 2 | 3.20 nm     | 1.96 nm               |
| Improvement 3 | 6.53 nm     | 1.96 nm               |

Both Improvement 1 and Improvement 3 make me highly confident the metrology can work. Improvement 2 could make-or-break the results, but is very close to the margin of error for theoretical calculations.

We can choose to use the lower voltages of ±12 V, supplied by fixed ±15 V regulators.

---

Regarding DAC power consumption, the PA95 datasheet shows 100 kΩ as the larger resistance of an inverting amplifier example. The datasheet also mentions 1 MΩ being an acceptable feedback resistor. With 0.2&ndash;0.5 pF parasitic capacitance, the R<sub>f</sub>C<sub>f</sub> pole would be 318&ndash;796 kHz.

| Small Resistor | Large Resistor | Current | Current x3 |
| -------------: | -------------: | ------: | ---------: |
| 2.8 kΩ         | 100 kΩ         | ±4.25 mA | ±12.75 mA |
| 28 kΩ          | 1 MΩ           | ±0.43 mA |  ±1.28 mA |

These currents are less than the ±15 mA drive capability of the DAC81404. We do not know whether this spec applies to each DAC channel individually, or the sum of all currents exiting the chip at any moment. Allowing ±45 mA out of the chip would actually not approach any limitation for the regulator. Phase 0.1 used LM78/LM79 instead of LM78L/LM79L. These support up to 1.5 A of current.

---

Other design simplifications today:
- Use just the 100 MΩ TIA instead of the 330 MΩ TIA. We are not working with extremely low currents like the Si + Si junction, which doesn't even show a detectable current at standard biases of 1 V. We are performing STM on conductors, not insulators. Typical currents are in the nanoamps.
- Use v<sub>bias</sub> only and not v<sub>comp</sub>. Even through Phase III, it's advantageous to avoid liquid nitrogen if possible. Bubbles in the evaporating liquid may cause vibrations, which require an internal isolator inside the UHV chamber. Cryo also may prevent optically guided tip approach. No need to test possibilities for capacitance sensing to improve usability of coarse tip approach, in the absence of optical guidance.
- The kinematic mount should also serve as the fine Z axis. If there are backlash problems (the simulations suggest so), just halve the range of the step from 408 nm to 204 nm. We can finally afford this because the range is now so large. And there's a very high chance someone got it working with 80 nm range.

There will be just one DAC chip, the DAC81401. Three of its ±12 V outputs will go to the three PA95 instances for later phases of the roadmap. The fourth output is the piezo control voltage in Phase 0.2, and the bias voltage in Phase II. Phase I just uses the first of the lines designated for PA95.

| Signal | Chip | Teensy Port |
| ------ | ---- | ----------- |
| fine X, 10 mm plates  | DAC81404 port 1 + PA95 | SPI0 |
| fine Y, 10 mm plates  | DAC81404 port 2 + PA95 | SPI0 |
| coarse Z, 5 mm plates | DAC81404 port 3 + PA95 | SPI0 |
| Phase 0.2 / v<sub>bias</sub> | DAC81404 port 4 | SPI0 |
| current | OPA828 + ADS8699 | SPI1 |
| capacitance | AD7745 | I2C |

We will assemble the board with reflow soldering, in the Controleo3 oven that also bakes epoxy. We will not engineer detachable PCBs just for failed DACs. <b>That drastically worsens design cost.</b> Instead, we will:
- Follow standard procedures for bypass capacitors and ESD mitigation. Use 0.1 μF + 10 μF, not 1 μF for the DAC. ADC will still use 1 μF + 10 μF.
- Use higher yield techniques: reflow soldering primarily, then higher tip temperature for hand soldering
- Order 5 spare chips for TSSOPs/QFNs and 5&ndash;6 copies of the PCB. We have the funds, and ~$252 extra here pales in comparison to ~$2500 for the commercial E-boxes.

## January 16, 2026

Two of these for Phase 0.2: https://www.amazon.com/Tekpower-TP3005T-Variable-Linear-Alligator/dp/B00ZBCLJSY

## January 20, 2026

I should use FreeCAD to create a professional, computer-generated technical drawing of my desired chamfer for LiNbO3 plates.

I can use these openly available dimensions to model the 650 V power supplies in FreeCAD: https://www.manualslib.com/manual/2615215/Matsusada-R4g-Series.html?page=18#manual

## January 24, 2026

[Vibration Isolation (Google Sheets)](https://docs.google.com/spreadsheets/d/1qzJEl3N8RIIDTsI8JntsrjS57pulaAYeZJ12WaDHFCc/edit?usp=sharing)

[Custom Isolator Investigation (Google Sheets)](https://docs.google.com/spreadsheets/d/1jo_KR99LT2sn_qSUho-MS6aLhETTfZkYWSGUg9xkJJw/edit?usp=sharing)

Eddy current damping is actually needed. Viton damping is superfluous and increases the mass of the STM table beyond acceptable limits (5 kg target mass). 

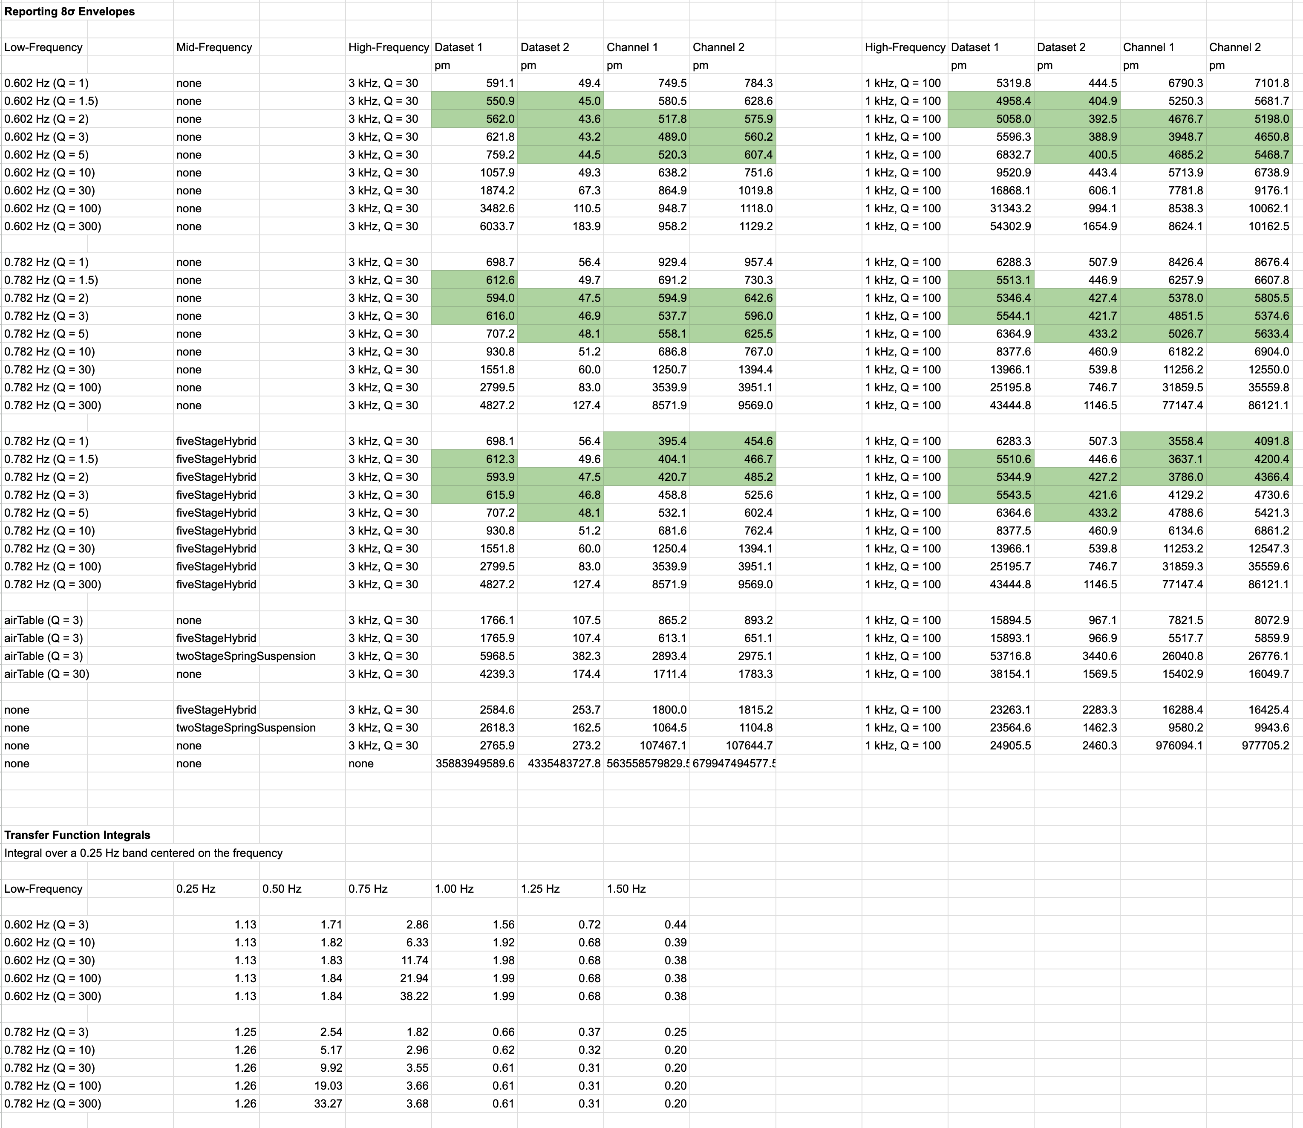
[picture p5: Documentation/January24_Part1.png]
January 24, Part 1


According to the above data, the optimal Q-factor is 2&ndash;5. 10 might not be bad, but 30 will definitely cause problems. Without eddy current damping, there's a very high chance the Q-factor is above acceptable limits.

I found a simple formula to calculate the Q-factor from the half-life of vibration amplitude. Note that amplitude and energy decay at different rates.

$Q = \frac{\pi}{\ln(2)} t_{1/2}$

$t_{1/2} = \frac{\ln(2)}{\pi} Q$

| Q-factor | Amplitude Half-Life |
| -------: | ------------------: |
| 1 | 0.22 |
| 1.5 | 0.33 |
| 2 | 0.44 |
| 3 | 0.66 |
| 5 | 1.10 |
| 10 | 2.21 |
| 30 | 6.62 |
| 100 | 22.06 |
| 300 | 66.19 |

_Data are in units of oscillation cycle count._

<b>Vertical and horizontal Q-factors are different</b> because the mechanism of magnetic field change is different for these two directions. People probably tune the Q-factor for the horizontal direction, with no rigorous treatment of the vertical Q-factor.

## January 26, 2026

I just ordered a massive bill of materials: $1,288.00

[Bill of Materials (Google Sheets)](https://docs.google.com/spreadsheets/d/1jiTSs0toMQvT6W_lkJ8dDeunRTFTPh3OK27fztuSNeY/edit?usp=sharing)

I recently finished a deal with Crystal Substrates. I paid approximately $1,500 and the desired quantity of spare LiNbO3 wafers will arrive in mid-March. I am also working on a deal with Matsusada, which will cost about $2,000 after tariffs. It will arrive in late February or early March.

Controleo3 reflow oven kits cost $395.00 and cannot be bought until January 31. I ordered the toaster oven itself in the above BOM.

Industry practice is to keep things secret. Quotes provided by hardware vendors are confidential information. I had to get approval from Matsusada to use the L x W x H dimensions in the open-source FreeCAD project (LabSpace.FCStd). However, it is important to disclose the true costs, especially given how revolutionary creepless SPM is, to save time for others trying to reproduce it. I concealed exact component costs not stated in the public catalog.

I based this vibration isolator on information from Weilin Ma and Dan Berard's public images. The benefit of open-source science is saving time for people trying to reproduce it in the future. Closed-source competitors like Nanofactory CBN Inc. and Quantum Silicon Inc. are wasting my time, gatekeeping information.

## January 29, 2026

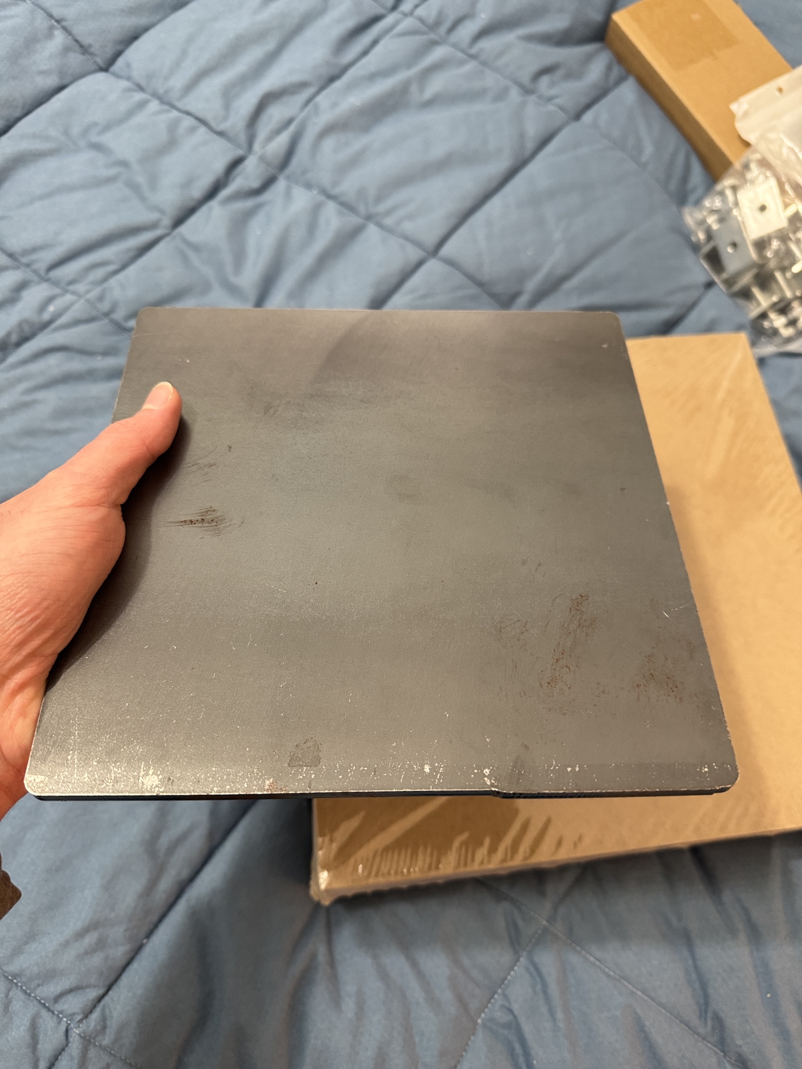
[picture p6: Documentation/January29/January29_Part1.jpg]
January 29, Part 1


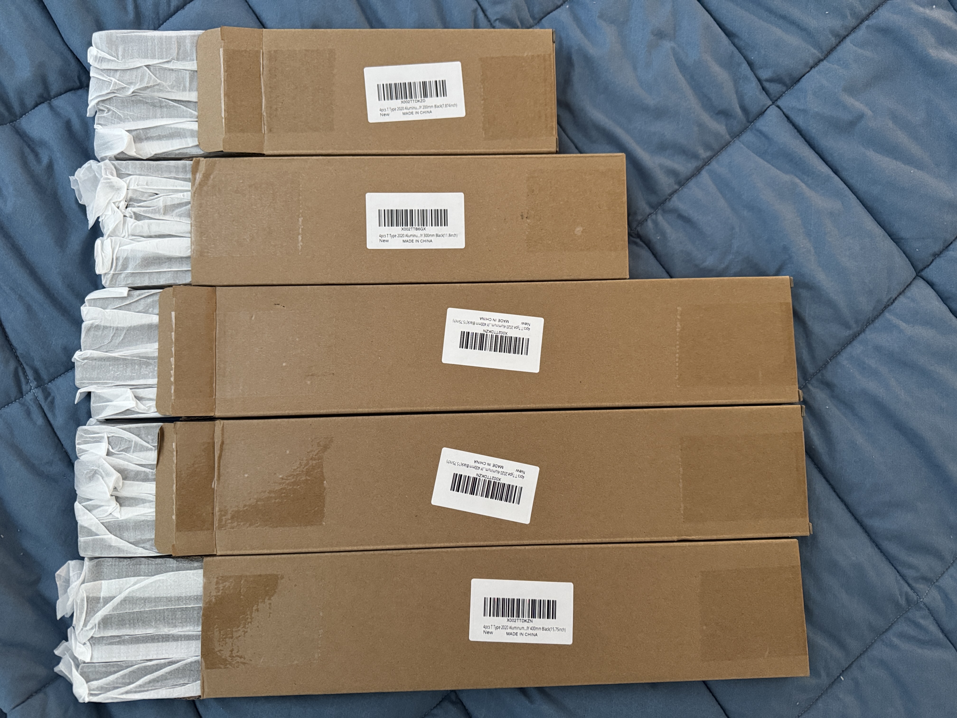
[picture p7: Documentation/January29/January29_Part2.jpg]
January 29, Part 2


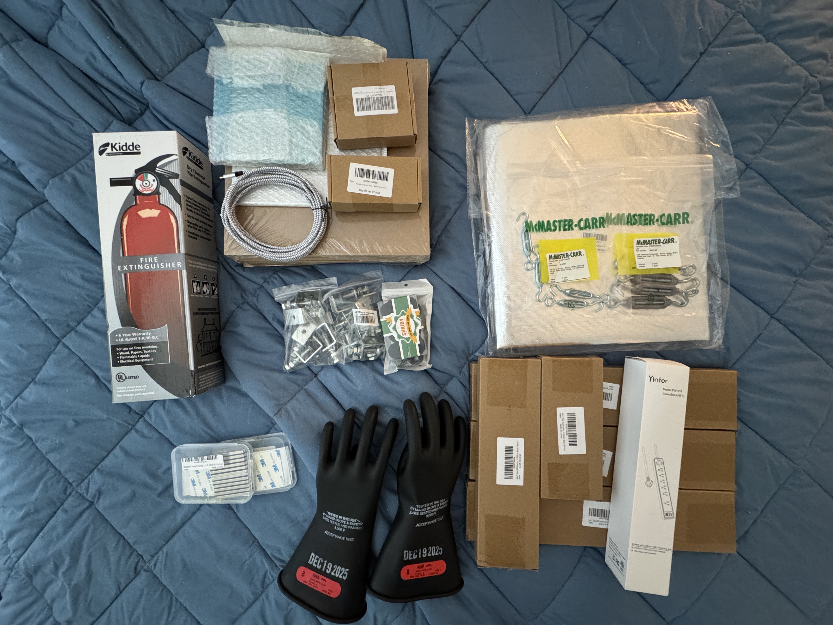
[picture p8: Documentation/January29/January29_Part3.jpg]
January 29, Part 3


## January 30, 2026

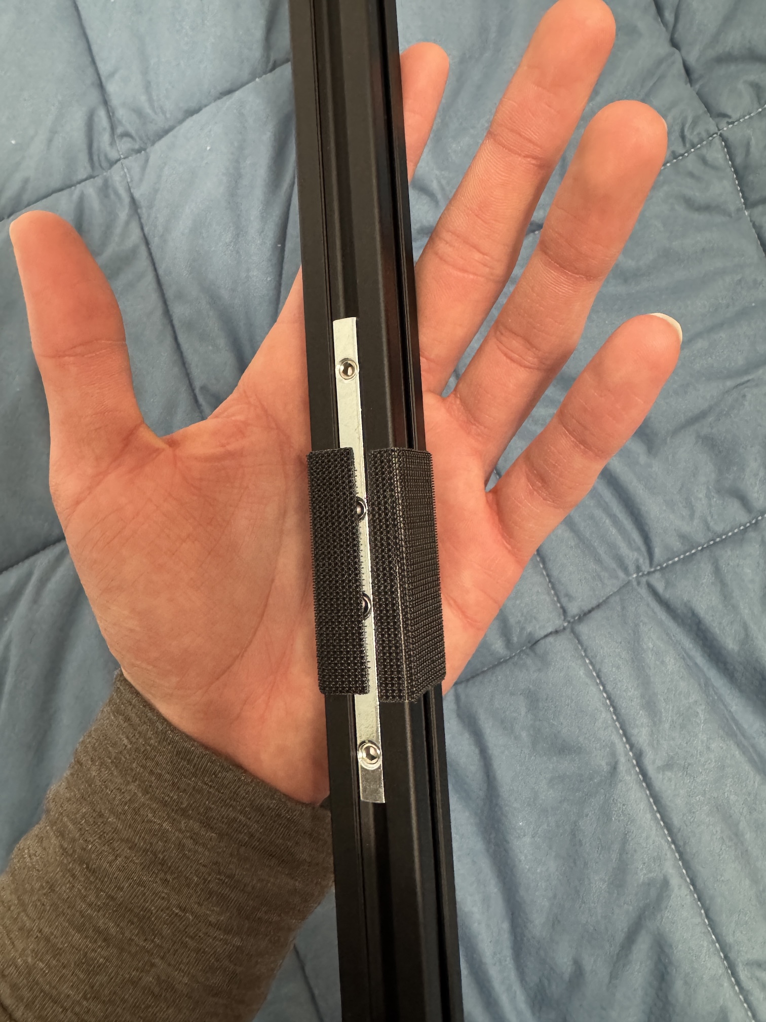
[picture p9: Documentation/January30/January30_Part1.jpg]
January 30, Part 1


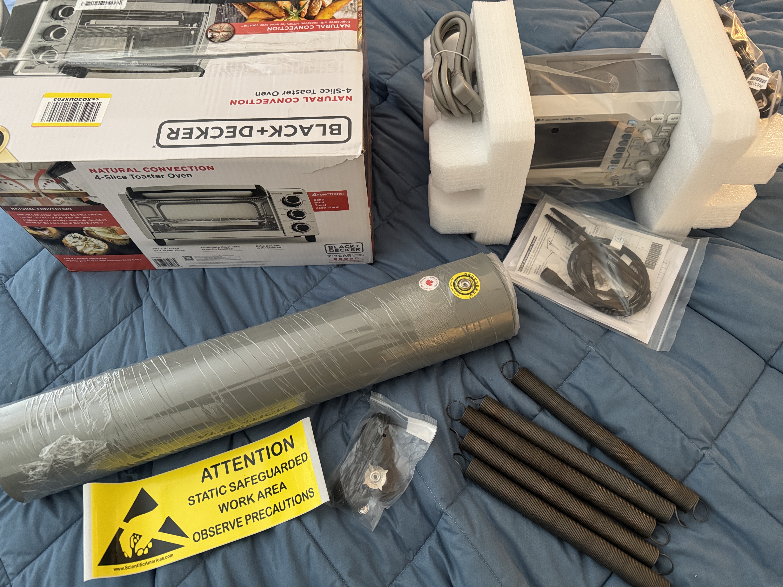
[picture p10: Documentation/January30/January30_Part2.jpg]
January 30, Part 2


I don’t know how, but both the vertical and horizontal resonances almost match the performance of Minus K isolators: 0.5 Hz. Dan Berard and others were 2.0 Hz. Best vibration isolator in the history of DIY STM (after Q-factor is reduced). 0.9 meters tall.

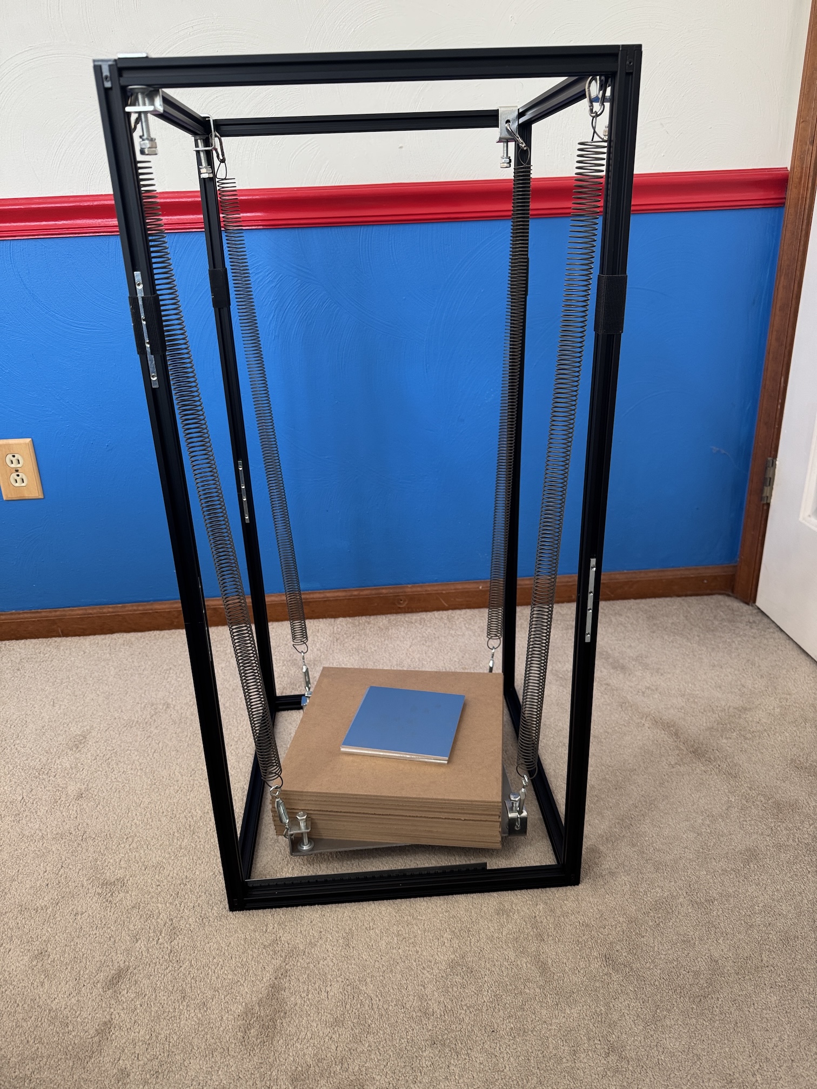
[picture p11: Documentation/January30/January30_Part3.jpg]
January 30, Part 3


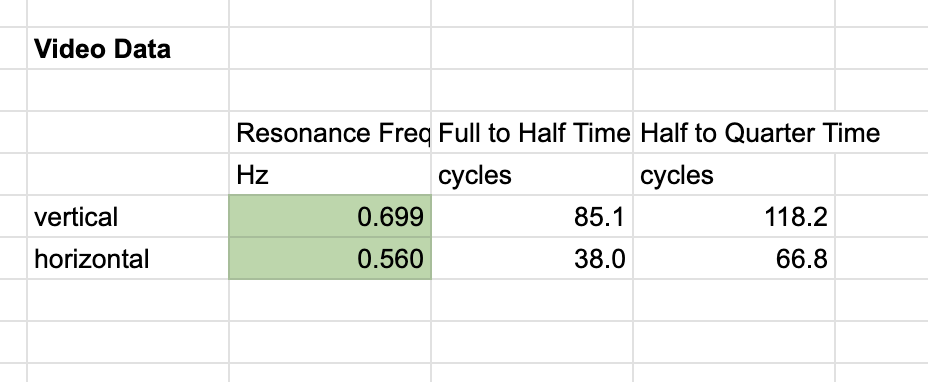
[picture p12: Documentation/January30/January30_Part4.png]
January 30, Part 4


<p align="center">
&nbsp;
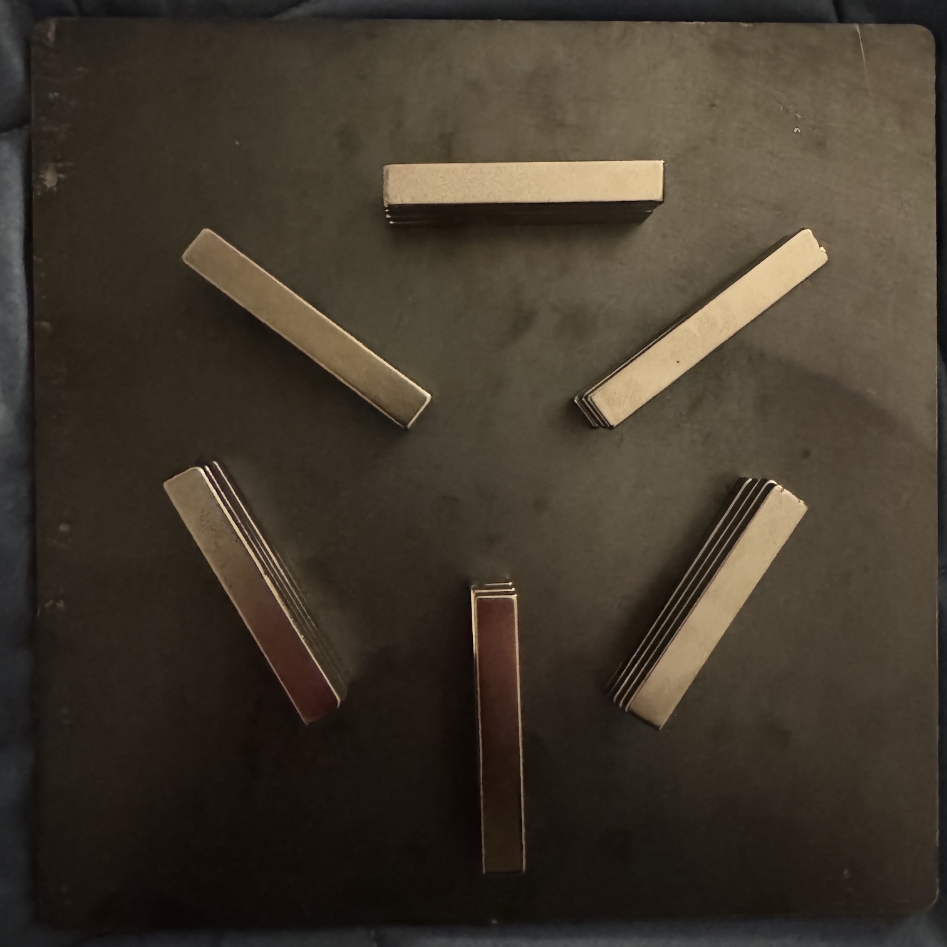
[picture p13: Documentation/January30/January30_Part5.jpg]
  
&nbsp;&nbsp;
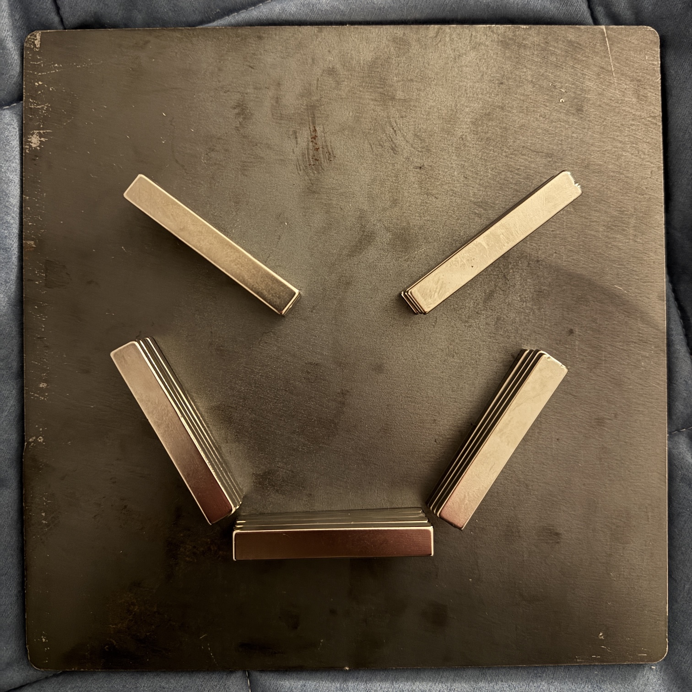
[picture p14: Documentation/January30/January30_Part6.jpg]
  
&nbsp;
</p>

## February 2, 2026

The Q-factor has been tuned. Close to 14 for both axes. Behavior of the Q-factor was slightly different than anticipated. The block of aluminum in the center indeed disproportionally damps Z more than XY. However, without the block, XY was about 38 and Z was about 25. So it doesn't make sense to widen a disparity in this direction (25 and 13).

I ended up with no special block of aluminum in the center, and just 0.65 cm distance from the magnets, instead of 1.3 cm. Analyzing each video took probably 10 minutes, and I didn't have the motivation to analyze 3 trials per configuration.

[Custom Isolator Investigation - Video Data (Google Sheets)](https://docs.google.com/spreadsheets/d/1jo_KR99LT2sn_qSUho-MS6aLhETTfZkYWSGUg9xkJJw/edit?gid=1881620548#gid=1881620548)

DIY VIBRATION ISOLATION SUB-PROJECT COMPLETE

### Recap

Current state of progress:
- All equipment on the BOM has arrived. Ordered the new Whizoo Controleo3 kit that just released.
- 99% finished with the Matsusada deal. Registered my corporation with Customs and Border Protection to import the two power boxes from Japan.
- Working through some revisions to the Crystal Substrates order. The technician says my first FreeCAD drawing is unrealistic, so we are figuring out alternatives.
- Having productive private discussions with CCDC/CSD-Core regarding organotins. Also good progress on the contract work with ChimiaDAO regarding both Ge and Sn tripods.
- About to have a private discussion with Scienta Omicron about the weird vacuum "doors" (load-lock chamber component) and a few other questions.
- All chips for the Phase 0.2/I/II PCB system have been decided. We also know the exact power supply voltages and a few protection diodes across the 450 V lines.

## February 3, 2026

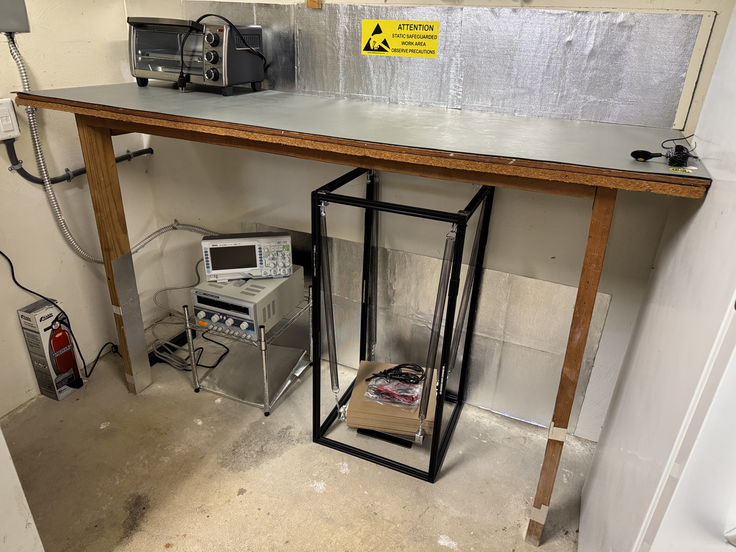
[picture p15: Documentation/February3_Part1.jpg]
February 3, Part 1


## February 11, 2026

I have answered many design questions about the PCBs. I was researching shielded RF connectors. The best approach is to start with mechanical design of Phase 0.2, I, II junctions. Work back from there.

Doing this step next will pave the way to answer the following questions:
- Which wires need to be coaxial?
- Are bulky SHV connectors actually needed for the piezo voltages?
- How do we prevent 430 V control voltages from coupling to sensitive parts like the ADC and preamp?
- What does the electromagnetic shielding look like?
- What is the length of connecting cables?

I need to figure out the exact connectors to use, but not the length of the cables. From that information, I can specify rough PCB dimensions and physical structure. Work back from that to figure out where electrical contacts are made on the STM junction. Finally, I can figure out the length of connecting cables.

The physical dimensions/layout of the STM and PCBs need to be resolved together. You cannot have one without the other. It's a paradox: neither is specified in enough detail yet. It's probably best to return to this problem tomorrow, when my mind is fresh.

---

I am deciding to reduce the scope of the PCB design work for Phase 0.2. I will build off the library of datasheets and symbols/footprints. I will use the same isolators, converters, regulators, and low-voltage power supply as Phase I/II. I am just archiving the 6 KiCad projects into a "PhaseI" folder, and continuing with a reduced subset.

Just looking at the Phase 0.2 capacitance junction, a 5 mm x 5 mm LiNbO3 piezo doesn't seem large enough to hold the weight of the associated plate. It looks mechanically unbalanced or wobbly. Moreso if a stack of 3 plates is used. I'll have to think very deeply about this.

---

I unpacked one of my 5 mm x 5 mm LiNbO3 plates for the first time, and tested a 14 mm x 16 mm x 16 mm pyrite cube on top of it. The cube balances and is mechanically stable. Just keep the center of mass over the piezo plate.

I will reproduce the Islam & Beamish junction as closely as possible, except the larger block has smaller dimensions (14 x 14 x 16 -> 10 x 10 x 12 mm). Both the ThorLabs plate and the existing LiNbO3 plates are 5 mm x 5 mm. I am not bothering with the complex setup from the Harvard (2024) paper, although I will take inspiration from how they arranged their electrodes and BNC connectors.

The Islam & Beamish paper used both machining and epoxy handling. I will have to get basic experience with both. This is a great, simple testing ground for learning these skills. Less demanding than a full STM body or multi-plate piezo stack.

I can also use copper foil to easily assemble a piezo stack held together by magnetism. This would triple the range of the LiNbO3 shear piezo. It is slightly different than stiffer "copper shim" used for piezo stacks. Actually, for non-UHV conditions, aluminum foil could be even more practical.

## February 12, 2026

A good, stiff STM should have a resonance frequency in the several kHz. When a mechanical device wobbles with a frequency in the single Hz range, something is wrong.

I tried assembling a stack of 3 plates, with electrodes made of two scraps of aluminum foil. It was very tedious to assemble: the stack kept falling apart, and I only got to balance the pyrite block on the 2nd attempt. When placing the block on the stack, it wobbled with a frequency in the single Hz range. When removing the foil and just stacking the flat plates themselves, the wobble disappeared. The same dichotomy happened with a LiNbO3 plate inside its plastic packaging, versus outside.

I split the two 5 mm x 12 mm scraps of aluminum foil into four 5 mm x 6 mm scraps. Then, I assembled the piezo stack like before, except odd and even electrode pairs weren't connected. This stack almost fell apart from the vibrations of something hitting the table. The pyrite block still wobbled when placed on top.

I tried omitting all electrodes except the piece of foil between the 1st and 2nd plate. The pyrite block still wobbled. Finally, I tried once more with only the piezo plates and no foil. The wobble did not exist. From this investigation, I can conclude that the simple "aluminum foil" piezo stack is impossible for Phase 0.2.

| Configuration | Piezo Stack | Balancing Pyrite Block |
| ------------- | ----------- | ---------------------- |
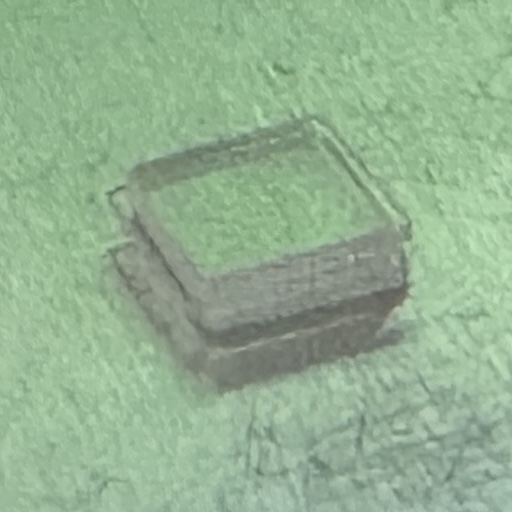
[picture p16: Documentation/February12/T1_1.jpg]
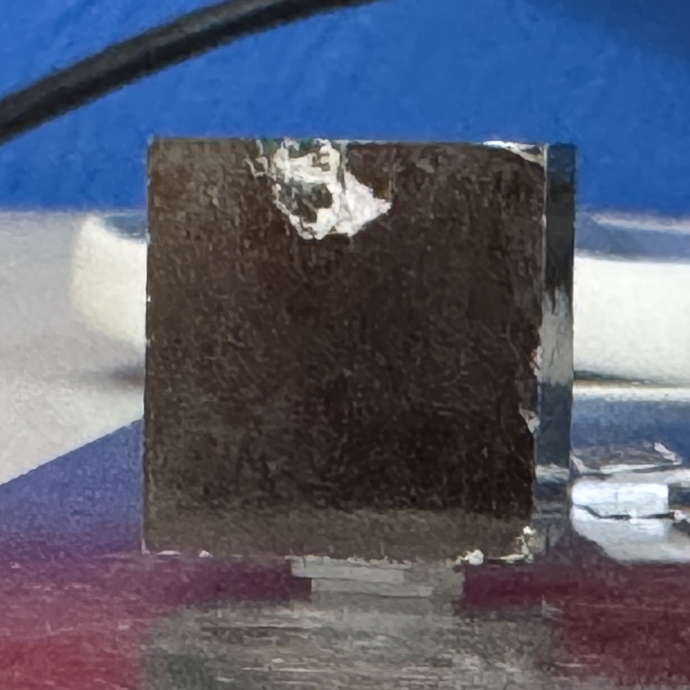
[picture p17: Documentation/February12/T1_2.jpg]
| only piezo plates    |  |  |
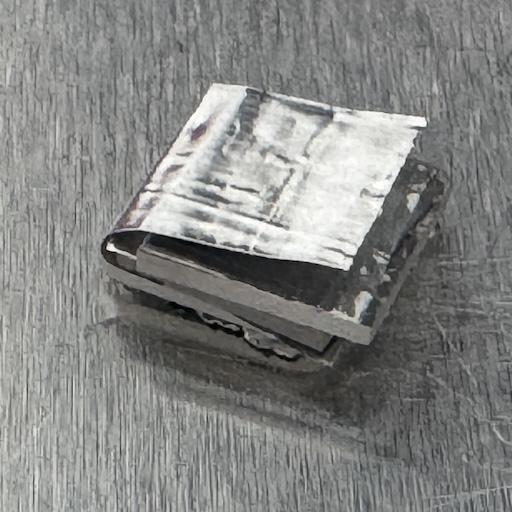
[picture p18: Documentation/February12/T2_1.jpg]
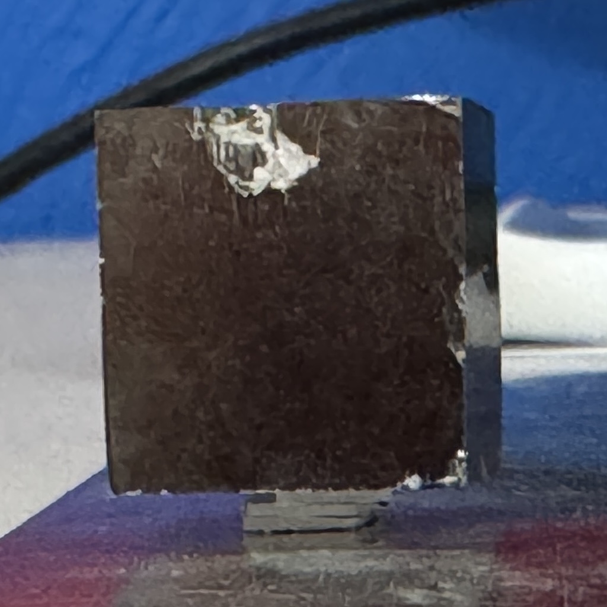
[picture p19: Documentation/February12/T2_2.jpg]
| two foil electrodes  |  |  |
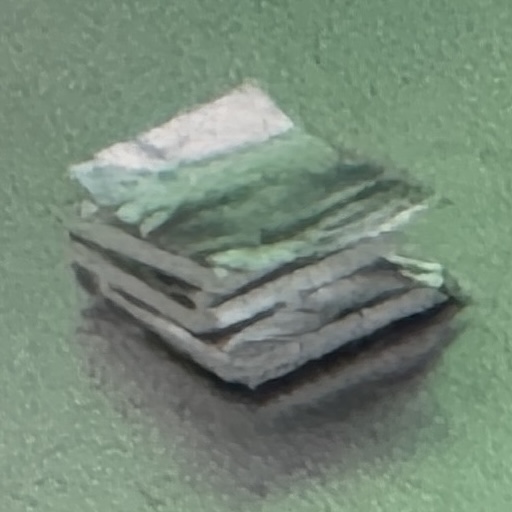
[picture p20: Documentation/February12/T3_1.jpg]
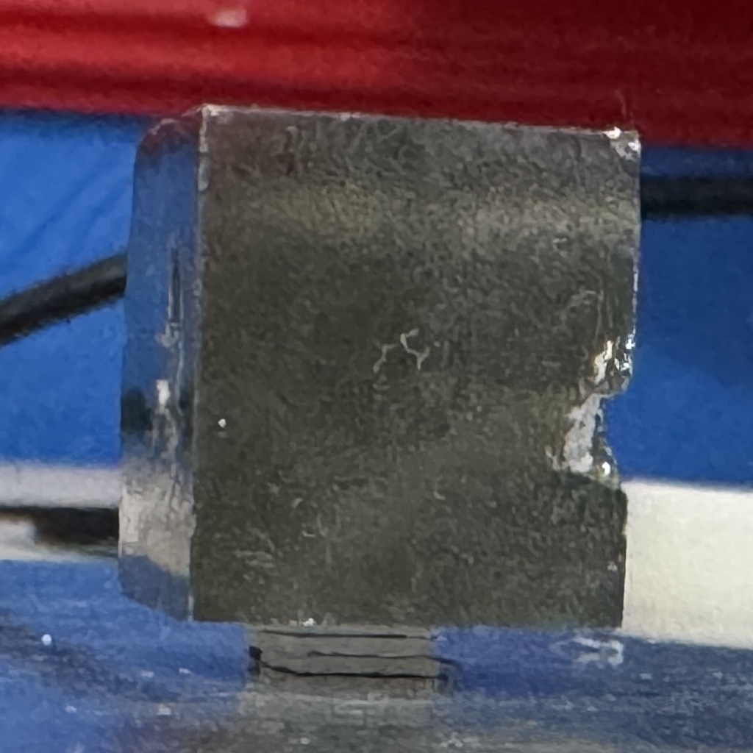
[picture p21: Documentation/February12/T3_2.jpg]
| four foil electrodes |  |  |
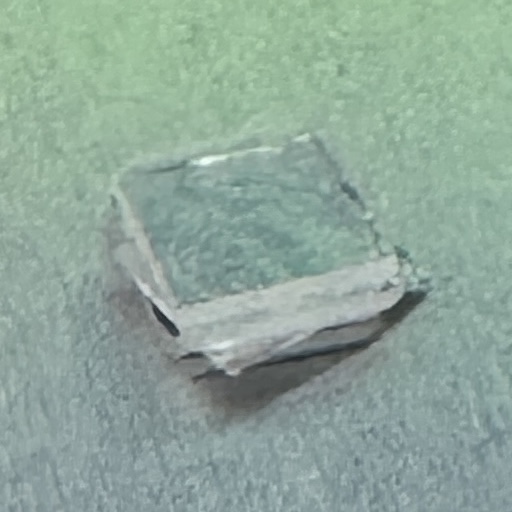
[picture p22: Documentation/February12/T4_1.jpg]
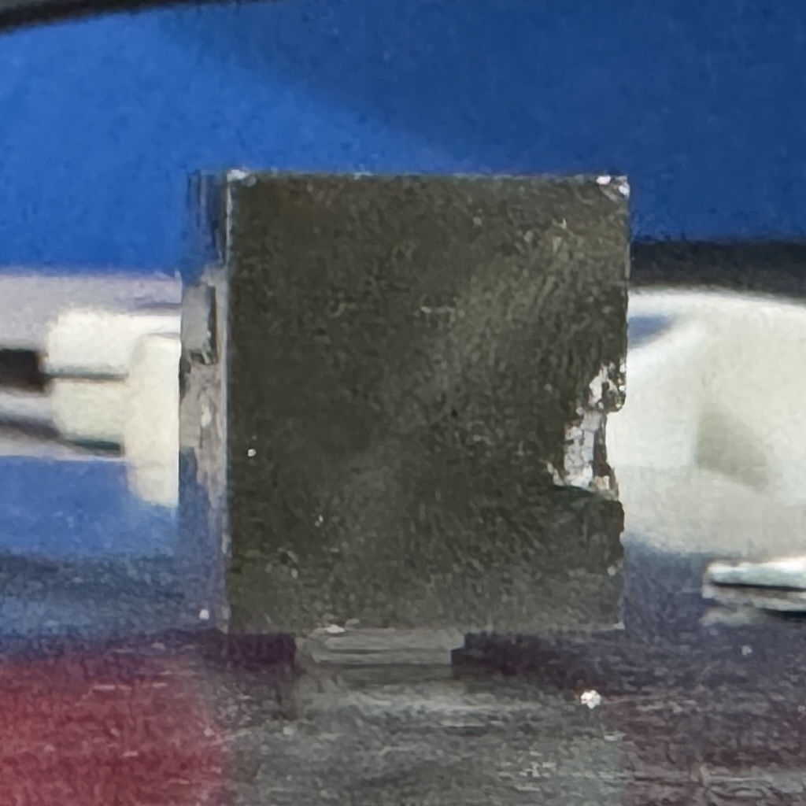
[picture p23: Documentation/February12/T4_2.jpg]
| one foil electrode   |  |  |

This wobbliness problem can appear anywhere in a mechanical system. It happens because two surfaces aren't held together by a strong force. To solve the problem, we need one of the following:
- large gravitational force
- magnetism
- chemical bonding (epoxy, solder)
- a spring clamp
- frictional force in a tightened screw, which is parallel to the contacting surfaces inside the screw

Everything but epoxy is a reversible connection mechanism. Solder can be undone and redone a small number of times, under the right conditions. The overarching problem is, if I mess up the layout of a mechanical system, there is no way to rearrange the existing parts. It would require buying the same individual parts all over again.

I can probably test certain subsystems for correct functioning before final assembly, such as a piezo stack. I can make the magnet force on the kinematic mount tunable, if both the top and bottom plates are made of steel. Many variables fall on a spectrum of tunability. But unfortunately, a few of them are probably 100% baked in ahead of time.

My task is to minimize the chance something goes wrong. Make as many connections as possible reversible, whether for practicality of storing the piece of hardware, or for correcting design errors. De-risk whenever possible. Accept the real possibility that I could run out of spare LiNbO3 piezo plates and face another 3-6 week lead time.

Too much fear of something going wrong will scare me away from trying anything.

## February 17, 2026

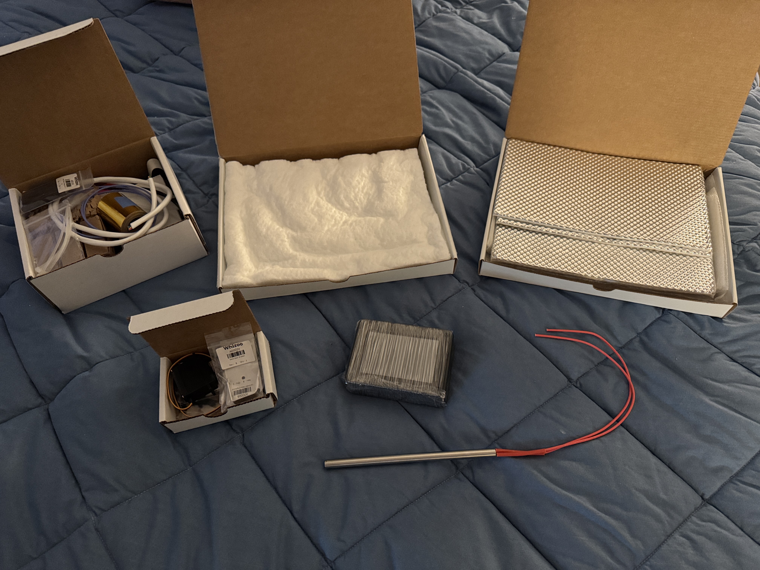
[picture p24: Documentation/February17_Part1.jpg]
February 17, Part 1


## February 27, 2026

[PCB BOM (Google Sheets)](https://docs.google.com/spreadsheets/d/11hSKUabHZscKTGl4hYCjbfahWj6xOX5oWkzyZ53yTAk/edit?usp=sharing)

## March 8, 2026

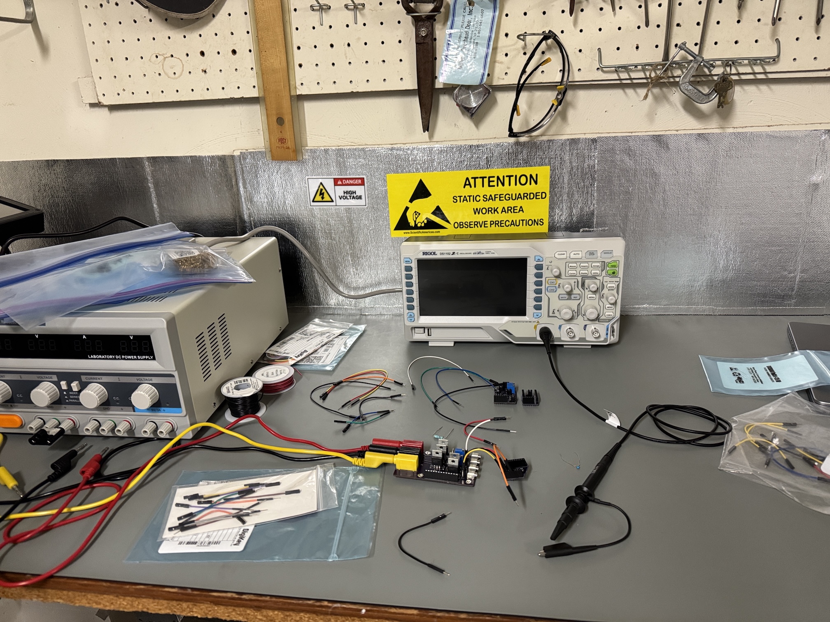
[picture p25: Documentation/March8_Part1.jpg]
March 8, Part 1


_Photograph of the lab setup for finding the bug._

I planned to test the frequency response of my transimpedance amplifiers today. However, TIA2 had 60 Hz interference with a magnitude of 2 V. While trying to understand the cause, I found a 2 V oscillation at 110 kHz in TIA1. This oscillation prevented me from measuring the 60 Hz interference in TIA1.

I have a theory about the cause. I accidentally reversed the supplies of TIA1. The regulators on the power board got extremely hot and I disconnected as soon as I noticed. Surprisingly, the op amp still worked after this event. But it could have caused unexplained degradations, just like ESD. Both the op amp and its bypass capacitors may have been affected.

I will test the 100 MΩ TIA on the Phase 0.1 board. If it doesn't show a 110 kHz oscillation, I will proceed with soldering a 2nd TIA1 from spare parts. In the process, I will also examine 60 Hz interference in the 330 MΩ TIA with the oscilloscope.

### Phase 0.1 Board

| Amplifier           | Osc. Freq. | Osc. Ampl. P-P |
| ------------------- | ---------: | -------------: |
| 100 MΩ              | 71 kHz     | 150 mV         |
| 330 MΩ              | 60 Hz      | 40 mV          |
| 330 MΩ              | >1 MHz     | 30 mV          |
| 330 MΩ (no limiter) | 180 kHz    | 30 V           |

I tested turning on the ±18 V linear power supply, just to see if it induced any noise from being nearby. There was no measurable effect.

## March 9, 2026

| Amplifier           | Osc. Freq. | Osc. Ampl. P-P |
| ------------------- | ---------: | -------------: |
| TIA1 (#1)           | 125 kHz    | 1.9 V          |
| TIA1 (#2)           | 125 kHz    | 1.9 V          |

I could not reduce the oscillation by increasing the C<sub>in</sub> capacitance between the two op amp terminals. I could reduce it marginally by placing large capacitors across R<sub>f</sub>.

| Capacitance | Osc. Freq. | Osc. Ampl. P-P |
| ----------: | ---------: | -------------: |
| ~0.1 pF     | 125 kHz    | 1.9 V          |
| 1 pF        | 125 kHz    | 380 mV         |
| 2 pF        | 125 kHz    | 210 mV         |
| 3 pF        | 125 kHz    | 150 mV         |
| 10 pF       | 125 kHz    | 50 mV          |
| 47 pF       | 125 kHz    | 15 mV          |

The ISO\_GND node is oscillating above oscilloscope case GND by 55 mV P-P at 125 kHz. But when I connect the second probe lead to the power board's GND, the oscillation vanishes. This oscillation was interfering with measurements of very small amplitude at 47 pF.

Just by being turned on, TIA1 injects a 60 mV oscillation into the PowerBoard GND, compared to the oscilloscope case GND. The oscillation doesn't happen when the power supply is turned off or TIA1 is disconnected.

C<sub>in</sub> of the op amp should be ~10 pF. The ground oscillation matches the oscillation after feedback when C<sub>f</sub> is ~10 pF. This is the point where noise gain is 1. At larger feedback capacitances, the noise gain shrinks.

I'll investigate the other TIA now and see whether it isn't horribly messed up. Perhaps OPA828 isn't a good chip, and the particular PCB layout choices for Phase 0.2 made it worse. I never noticed the problem much in Phase 0.1 because the 2nd-order LPF at 15 kHz greatly reduced the magnitude of the 71 kHz oscillation. However, the oscilloscope trace now will show a massive noise band of 150 mV.

---

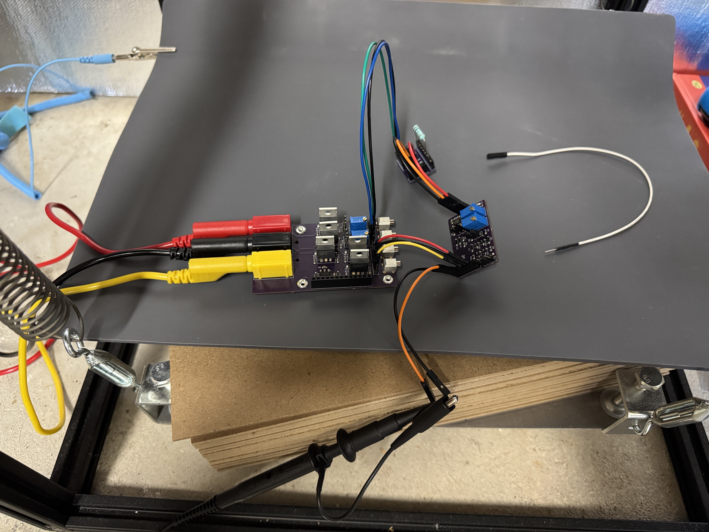
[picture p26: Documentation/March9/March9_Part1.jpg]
March 9, Part 1


_Reproduction of the setup that caused concern about 60 Hz noise with TIA2._

I set up TIA2 and measured interference with the setup above.

| Amplifier           | Osc. Freq. | Osc. Ampl. P-P |
| ------------------- | ---------: | -------------: |
| TIA2                | 120 Hz     | 300 mV         |
| TIA2                | 125 kHz    | 400 mV         |
| TIA2                | 1.5 MHz    | 800 mV         |

This time, the 125 kHz oscillation does not appear when I try to measure the PowerBoard GND compared to the oscilloscope case. However, when I disconnect the GND clip of the probe, the 125 kHz oscillation's magnitude jumps to 1.0 V. This signal dominates the noise band, making it hard to see how 120 Hz noise changes when disconnecting the GND clip.

By placing a steel tray next to the boards, and bringing out a GND wire from the power board, I can decimate the magnitude of 125 kHz interference...

Will experiment with doing this for TIA1.

---

| Amplifier | Shield | Osc. Freq. | Osc. Ampl. P-P |
| --------- | ------ | ---------: | -------------: |
| TIA1 | none | 125 kHz | 1.9 V, 2.8 V |
| TIA1 | vibration isolation table | 125 kHz | 1.9 V, 2.8 V |
| TIA1 | reflow oven | 125 kHz | 1.9 V, 2.8 V |
| TIA2 | none | 120 Hz | 200&ndash;400 mV |
| TIA2 | none | 125 kHz | 200 mV |
| TIA2 | none | 1.5 MHz | 500 mV |
| TIA2 | vibration isolation table | 120 Hz | 20 mV |
| TIA2 | vibration isolation table | 125 kHz | 60 mV |
| TIA2 | vibration isolation table | 1.5 MHz | 100 mV |
| TIA2 | reflow oven | 125 kHz | 90 mV |

_Including a re-evaluation of TIA2 with no shield, to rule out the effect of some wires being shortened._

The oscillation in TIA1 cannot be suppressed with shielding. I don't even know what's going so wrong, but I can do STM with only TIA2. Fixing TIA1 will probably be a waste of time.

The only way to reduce noise even more, is probably a seamless shield with no hole larger than a specific wavelength. Attempts to enhance existing shielding will probably be a waste of time.

---

Let's examine the frequency response and then make more decisions about shielding. I might want to repurpose some pins used for connecting PowerBoard to MainBoard, so they serve as receptacles for AWG 22 wire.

---

| Amplifier | Configuration | Voltage | ADC Filtered | Current |
| --------- | ------------: | ------: | -----------: | ------: |
| 100 MΩ | Phase 0.1     | 150 mV | 7 mV   |
| 100 MΩ | Phase 0.2     | 2.8 V  | 40 mV  |
| 100 MΩ | 0.95 m shield | 2.8 V  | 40 mV  |
| 100 MΩ | 0.29 m shield | 2.8 V  | 40 mV  |
| 330 MΩ | Phase 0.1     | 40 mV  | 40 mV  |
| 1 GΩ   | no shield     | 500 mV | 200 mV |
| 1 GΩ   | 0.95 m shield | 150 mV | 20 mV  |
| 1 GΩ   | 0.29 m shield | 90 mV  | ~0 mV  |

| Amplifier | Configuration | Current | ADC Filtered |
| --------- | ------------: | ------: | -----------: |
| 100 MΩ | Phase 0.1     | 1.5 nA | 70 pA  |
| 100 MΩ | Phase 0.2     | 28 nA  | 400 pA |
| 100 MΩ | 0.95 m shield | 28 nA  | 400 pA |
| 100 MΩ | 0.29 m shield | 28 nA  | 400 pA |
| 330 MΩ | Phase 0.1     | 120 pA | 120 pA |
| 1 GΩ   | no shield     | 500 pA | 200 pA |
| 1 GΩ   | 0.95 m shield | 150 pA | 20 pA  |
| 1 GΩ   | 0.29 m shield | 90 pA  | ~0 pA  |

_From the dimensions of the aluminum T-slot frame, the largest aperture size in the vibration isolator is 0.95 m. The reflow oven's largest aperture size is 0.29 m._

---

[Tuning frequency response of 1 GΩ transimpedance amplifier (YouTube)](https://www.youtube.com/watch?v=ghyBSe6H7iE)

EMI after tuning frequency response:

| Amplifier | Shield | Osc. Freq. | Osc. Ampl. P-P |
| --------- | ------ | ---------: | -------------: |
| TIA2 | none | combined | 600 mV |
| TIA2 | none | 120 Hz | 200 mV |
| TIA2 | none | 125 kHz | 200 mV |
| TIA2 | none | 1.5 MHz | 300 mV |
| TIA2 | vibration isolation table | combined | 150 mV |
| TIA2 | vibration isolation table | 120 Hz | 30 mV |
| TIA2 | vibration isolation table | 125 kHz | 80 mV |
| TIA2 | vibration isolation table | 1.5 MHz | 80 mV |

---

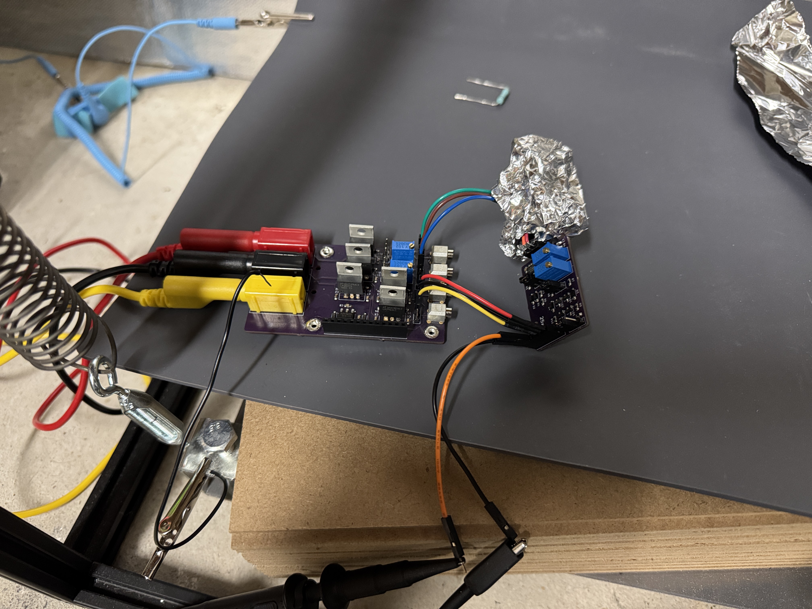
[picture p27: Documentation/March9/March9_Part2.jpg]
March 9, Part 2


I created this small enclosure for the preamp out of aluminum foil, lined with parchment paper to prevent shorts from contacting the PCB. It serves as a functioning standalone enclosure, isolating noise to 150 mV regardless of whether the vibration isolator is electrically connected.

120 Hz and 1.5 MHz signals are, for the most part, annihilated. Only the 125 kHz signal remains. It was like this for the reflow oven as well (a much better shield than the vibration isolator). It is also quite interesting that the 125 kHz signal is approximately this magnitude (100&ndash;200 mV) both with and without shielding. That tells me the situation could be similar to TIA1. Not a good sign.

---

TIA1 on the Phase 0.1 board shows a 125 kHz, 2.8 V oscillation when wired to the wall power supply for Phase 0.2. 

Next tests:
- Isolated battery supply (again)
  - 69 kHz, 100 mV
- <s>Wall power supply, powering regulators from Phase 0.1 board</s>
- Changing wall power supply from ±18 V to ±27 V
  - ~100 kHz, 1.9 V
- Wall power supply, powering regulators from Phase 0.1 board (±18 V)
  - 70 kHz, 150 mV
- Wall power supply, powering regulators from Phase 0.1 board (±26 V)
  - 70 kHz, 150 mV
- Batteries, powering Phase 0.2 regulators
  - 140 kHz, 200 mV
- <s>Soldering 1N4007W diodes onto Phase 0.1 board</s>
- Removing the 1N4007W diodes from Phase 0.2, -15 V and 15 V regulators
  - 125 kHz, 1.9 V

It is very hard to set the midpoint of the voltage range on the oscilloscope display. I could measure a faint, <100 mV oscillation on the -15 V supply when TIA1 is plugged in and oscillating at 1.9 V. When I disconnect TIA1, the -15 V supply doesn't show a faint, barely-detectable ripple.

When I connected the oscilloscope probe between GND and -15 V in the wrong order, the oscilloscope showed weird signals and the regulators got extremely hot. I turned off the circuit immediately. This is the second instance of such an overcurrent event.

I need to double check once more that wall power can make TIA1 work cleanly, using the regulators on the Phase 0.1 board. Test TIA1 on the Phase 0.1 board and bring the supply lines out to Phase 0.2 TIA1. Also, try once more to disconnect the power supply from case GND to rule out a ground loop. And test whether the internal short between the master and slave power channels doesn't have weird quirks. Try changing the 0.1 uF output capacitor of a 15 V regulator to 1 uF. Perhaps the recommended 2.2 uF for the negative regulator was truly needed. But it's already 10:00 PM, so I'll have to pick up where I left off tomorrow.

## March 10, 2026

I found a solution to the problem! Add a large electrolytic capacitor to the output of the -15 V regulator.

Connecting the -15 V output to the Phase 0.1 board raises its output capacitance tremendously, from 1.1 uF to 4.1 uF. But even just an extra 1 uF mylar capacitor on a breadboard will decimate the oscillation. For better performance, polarized electrolytics do a better job with the same capacitance. 10 uF electrolytic is very good, and 100 uF is best. Positive supply doesn't show any change in behavior when attaching more capacitors.

| Capacitor Type | Capacitance | TIA1 Osc. P-P |
| -------------- | ----------: | ------------: |
| none           | none        | 2.8 V |
| mylar          | Phase 0.1 board | 100 mV |
| mylar          | 1 uF | 120 mV |
| electrolytic   | 1 uF | 70 mV |
| mylar          | 2.2 uF | 100 mV |
| electrolytic   | 2.2 uF | 50 mV |
| mylar          | 4.4 uF | 90 mV |
| electrolytic   | 4.7 uF | 40 mV |
| electrolytic   | 10 uF  | 35 mV |
| electrolytic   | 20 uF  | 30 mV |
| electrolytic   | 47 uF  | 30 mV |
| electrolytic   | 100 uF | 20 mV |
| mixed          | Phase 0.1 + 100 uF | 20 mV |
| electrolytic   | 200 uF | 15 mV |

I should also test the behavior of the 1 GΩ or 330 MΩ transimpedance amplifiers. They are more complex, because two negative regulators could mess things up.

---

EMI before modifying bypass capacitors, with power lines brought out to breadboard:

| Amplifier | Shield | Osc. Freq. | Osc. Ampl. P-P |
| --------- | ------ | ---------: | -------------: |
| TIA2 | none | combined | 2.0 V |
| TIA2 | none | 120 Hz | 1.0 V |
| TIA2 | none | 125 kHz | 500 mV |
| TIA2 | none | 1.5 MHz | 500 mV |
| TIA2 | vibration isolation table | combined | 600 mV |
| TIA2 | vibration isolation table | 120 Hz | TBD |
| TIA2 | vibration isolation table | 125 kHz | 400 mV |
| TIA2 | vibration isolation table | 1.5 MHz | TBD |

Adding a large bypass capacitor across the -5 V line did not help. But adding one across -15 V did. I'll measure the behavior of -15 V, then redo the wiring to reduce coupling into the preamp's power supplies.

Adding a 100 uF bypass capacitor across -15 V for OP37G:

| Amplifier | Shield | Osc. Freq. | Osc. Ampl. P-P |
| --------- | ------ | ---------: | -------------: |
| TIA2 | vibration isolation table | combined | 400 mV |
| TIA2 | vibration isolation table | 120 Hz | 300 mV |
| TIA2 | vibration isolation table | 125 kHz | 200 mV |
| TIA2 | vibration isolation table | 1.5 MHz | 50 mV |

---

New setup for wiring:

| Amplifier | Configuration | Osc. Freq. | Osc. Ampl. P-P |
| --------- | ------ | ---------: | -------------: |
| TIA2 |  | combined | 600 mV |
| TIA2 |  | 120 Hz | 200&ndash;400 mV |
| TIA2 |  | 125 kHz | 150 mV |
| TIA2 |  | 1.5 MHz | 300 mV |
| TIA2 | 0.95 m shield | combined | 150 mV |
| TIA2 | 0.95 m shield | 120 Hz | 30&ndash;60 mV |
| TIA2 | 0.95 m shield | 125 kHz | 100 mV |
| TIA2 | 0.95 m shield | 1.5 MHz | 50 mV |
| TIA2 | 0.95 m shield + 100 uF | combined | 90 mV |
| TIA2 | 0.95 m shield + 100 uF | 120 Hz | 35&ndash;70 mV |
| TIA2 | 0.95 m shield + 100 uF | 125 kHz | 40 mV |
| TIA2 | 0.95 m shield + 100 uF | 1.5 MHz | 60 mV |

Adding the foil shield back. Connecting the vibration isolator shield simultaneously does not reduce noise any further. This is a bit frustrating, as the vibration isolator shield alone has 150 mV total noise. This is less than the 300 mV total with the foil shield.

| Amplifier | Configuration | Osc. Freq. | Osc. Ampl. P-P |
| --------- | ------ | ---------: | -------------: |
| TIA2 | foil shield | combined | 300 mV |
| TIA2 | foil shield | 120 Hz | ~0 mV |
| TIA2 | foil shield | 125 kHz | 250 mV |
| TIA2 | foil shield | 1.5 MHz | ~0 mV |
| TIA2 | foil shield + 100 uF | combined | 80 mV |
| TIA2 | foil shield + 100 uF | 120 Hz | ~0 mV |
| TIA2 | foil shield + 100 uF | 125 kHz | ~0 mV |
| TIA2 | foil shield + 100 uF | 1.5 MHz | ~0 mV |

So the 125 kHz signal has vanished. Next, I will investigate how total noise and 125 kHz interference scale with capacitor size. Larger ones take a long time to discharge, and I fetched a 100 kΩ bleeder resistor for it.

| Amplifier | Capacitor | Osc. Freq. | Osc. Ampl. P-P |
| --------- | -----: | ---------: | -------------: |
| TIA2 | none | combined | 300 mV |
| TIA2 | none | 125 kHz | 250 mV |
| TIA2 | 10 nF mylar | combined | 300 mV |
| TIA2 | 10 nF mylar | 125 kHz | 250 mV |
| TIA2 | 47 nF mylar | combined | 150 mV |
| TIA2 | 47 nF mylar | 125 kHz | 130 mV |
| TIA2 | 100 nF mylar | combined | 90 mV |
| TIA2 | 100 nF mylar | 125 kHz | 90 mV |
| TIA2 | 200 nF mylar | combined | 80 mV |
| TIA2 | 200 nF mylar | 125 kHz | 50 mV |
| TIA2 | 1 uF mylar | combined | 70 mV |
| TIA2 | 1 uF mylar | 125 kHz | 30 mV |
| TIA2 | 1 uF electrolytic | combined | 80 mV |
| TIA2 | 1 uF electrolytic | 125 kHz | 40 mV |
| TIA2 | 4.4 uF mylar | combined | 70 mV |
| TIA2 | 4.4 uF mylar | 125 kHz | 20 mV |
| TIA2 | 100 uF electrolytic | combined | 90 mV |
| TIA2 | 100 uF electrolytic | 125 kHz | 20 mV |

I'm going to add a 10 uF, 0805 ceramic capacitor on top of the existing output capacitor for the -15 V regulator. I will not re-install the 1N4007W protection diodes. This choice has the least amount of effort to rework soldered parts. Then, I will test the performance of the new power board with TIA1 and TIA2.

As a recap, these are the P-P amplitudes of the 70&ndash;125 kHz oscillation:
- With 1 uF output capacitor across -15 V:
  - TIA1: 1.9 V or 2.8 V
  - TIA2: 150&ndash;250 mV (500 mV under rare conditions)
- With 2.1 uF combined unpolarized capacitance:
  - TIA1: 120 mV
  - TIA2: 30 mV
- With 3.1&ndash;4.1 uF from Phase 0.1 board connection:
  - TIA1: 100&ndash;150 mV
  - 330 MΩ: undetectable
- With 5.5 uF unpolarized:
  - TIA1: 90 mV
  - TIA2: 20 mV
- With 5.8&ndash;10.8 uF polarized:
  - TIA1: 35&ndash;40 mV
  - TIA2: 20 mV
- With 100 uF polarized:
  - TIA1: 15 mV
  - TIA2: 20 mV

---

| Amplifier | Shield | Osc. Freq. | Osc. Ampl. P-P |
| --------- | ------ | ---------: | -------------: |
| TIA1 | none | combined | 250 mV |
| TIA1 | none | 120 Hz | 0 mV |
| TIA1 | none | 67 kHz | 100 mV |
| TIA1 | none | 1.7 MHz | 40 mV |
| TIA1 | vibration isolation table | combined | 200 mV |
| TIA1 | vibration isolation table | 120 Hz | 0 mV |
| TIA1 | vibration isolation table | 67 kHz | 100 mV |
| TIA1 | vibration isolation table | 1.7 MHz | 0 mV |
| TIA2 | foil shield | combined | 80 mV |
| TIA2 | foil shield | 120 Hz | 0 mV |
| TIA2 | foil shield | 125 kHz | 0 mV |
| TIA2 | foil shield | 1.5 MHz | 0 mV |

### Redo of Frequency Response Analysis

March 10, Part 1

_Oscilloscope trace of frequency response. Amplifier: TIA1, DUT: 1.7 pF, triangle wave: 15.0 V/ms rising, -11.8 V/ms falling. Bandwidth is predicted to be 10 kHz._

March 10, Part 2

_Oscilloscope trace of frequency response. Amplifier: TIA2, DUT: 0.4 pF, triangle wave: 4.80 V/ms rising, -3.78 V/ms falling. Bandwidth is predicted to be 45 kHz._

The trace for TIA2 looks sharper than in the video because 125 kHz interference is removed. In addition, shielding against 120 Hz interference may have stopped the bottom side of the square wave from showing a random broadening of its noise band to ~0.5 V. The small oscillations that quickly decay after the voltage jump have ~200 kHz frequency.

Tuned variables:
- Pre-amplifier positive supply:
  - 2.8 V before plugging in
  - 2.5 V after plugging in
- Pre-amplifier negative supply:
  - -1.8 V before plugging in
  - -1.5 V after plugging in
- Post-amplifier:
  - RV1 = 470 Ω
  - RV2 = 78.4 kΩ

## March 12, 2026

I am attempting to debug the problem that prevents SPI from reaching maximum rates of 40&ndash;50 MHz with the ADS8699. The Phase 0.1 board started dropping bits at 21.8 MHz. The current board drops them at 18&ndash;19 MHz.

I analyzed the signals with the oscilloscope, and the clock signal starts getting very deformed at around 20 MHz. At lower speeds, it reaches a long plateau. At higher speeds, it becomes a triangle wave. The problem originates in the Teensy itself, not the SPI isolator. The Teensy's rising edge settles in 20 ns, far longer than the expected rise time.

Supposedly, the Teensy cannot run SPI at more than 30 MHz. Some people reported flaky situations where one person did a thing at 40 MHz, but another person struggled to reproduce it at only 24&ndash;26 MHz.

One suspected solution is adding 50&ndash;220 Ohm resistors near the Teensy's pins. Since a 50 Ohm resistor to ground would cause an insane amount of current, I must instead wire the resistor in series with the signal line.

The series resistor could shape the SCK waveform. In a certain wiring configuration, the oscilloscope measures an overshoot on the SCK signal. Adding a 50 Ohm resistor made it undershoot. Larger resistors were worse. 33 Ohms was the sweet spot. But the rise time was still 10 or 20 ns.

Adding 10 or 50 Ohm resistors in series with MOSI, MISO, and CS produced unexplainable results. Certain configurations reduced the maximum speed to 15&ndash;16 MHz or 17&ndash;18 MHz. Nothing increased the speed to 19 MHz or higher.

I tried adding an extra 1 uF mylar capacitor across the Teensy's 3.3V and ground. It did not reduce the rise time. Even a 10 uF electrolytic capacitor did not. The Teensy's technical drawing shows many bypass capacitors, including a 4.7 uF one.

I will try the following solutions next:
- Add an extremely large bypass cap (100 uF electrolytic) and see whether SCK rise time improves
- Study the strange instance where I measured low (1&ndash;2 V) output voltages from the MISO pin on the ADC
- Study how the DAC chips behave

---

The 100 uF bypass capacitor across 3.3V did not work. Rise times are the same, cutoff frequency is still 18&ndash;19 MHz. Putting it across the 5V pin next to 3.3V and GND also does not work.

<p align="center">
&nbsp;
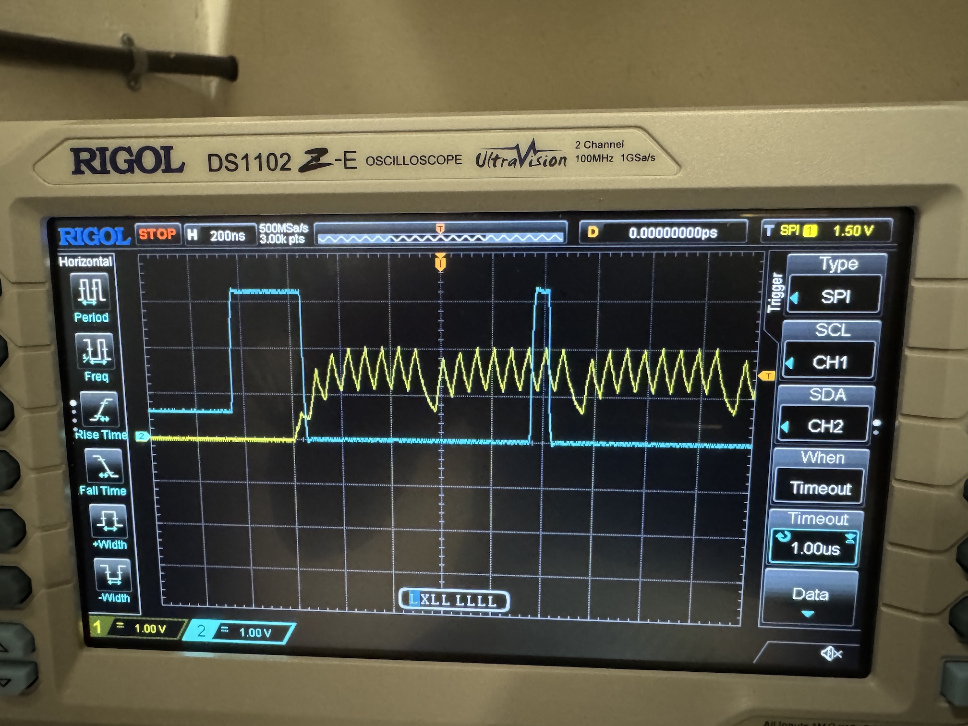
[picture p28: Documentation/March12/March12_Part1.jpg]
  
&nbsp;&nbsp;
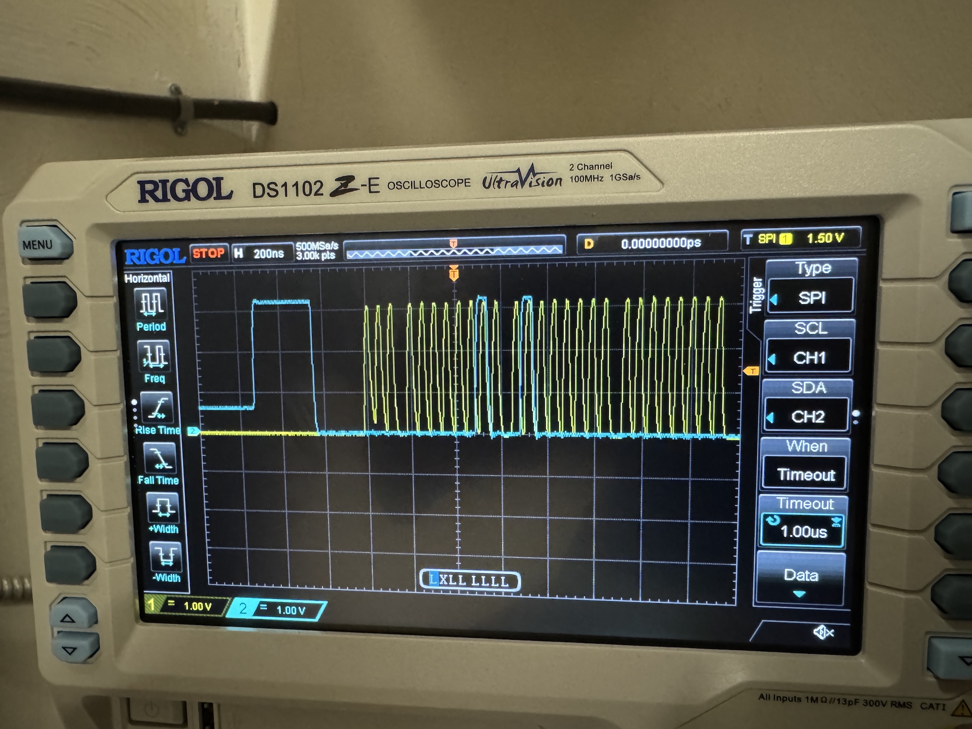
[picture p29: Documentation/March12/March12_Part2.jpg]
  
&nbsp;
</p>

_<b>Left:</b> Trace taken at 15 MHz. SCK (yellow) has half the correct magnitude, but this is a measurement artifact. <b>Right:</b> Trace taken at 20 MHz. Have not gathered enough samples to know whether this disparity is random, or the extra bit comes from errors at 20 MHz._

The low signal voltage for MISO was a false lead. All tests show 3.3V at both 15 MHz and 20 MHz. I think, after 20 MHz, an extra bit appears in the oscilloscope trace. Since it's two apart from the other bit (not zero apart), I cannot see how it would correspond to a change from 0.5 to 0.75 in binary. I also do not understand the endianness of integers for converting to `float` after shifting 14 bits.

I tried to use the `adcResponsivenessDiagnosticLoop` with 15 MHz vs. 20 MHz for the SPI transactions. The ADC stops responding to range-select changes at 20 MHz.

Next, I will clean up the code from debugging and test the DAC81401. Hopefully, it does not shut down randomly and break from sustained damage. Then, I can study its behavior at high SPI speeds.

## March 20, 2026

Link to the new BOM (plan to order tomorrow): [Next BOM (Google Sheets)](https://docs.google.com/spreadsheets/d/1qZ6N7xbDPV2qiAkH7os0ZhyjvyFWOlCQFE3YEBIGxq4/edit)

## March 26, 2026

[Measuring a 3 picofarad capacitor to 10 attofarad precision (YouTube)](https://www.youtube.com/watch?v=1fGW8lledkQ)
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

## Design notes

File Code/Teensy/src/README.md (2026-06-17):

# Notes

Sections of the code that are sometimes disabled for debugging, but should be re-enabled during normal STM operation:
- `KilohertzLoop` checks for timing drift
- `IC::Validation` checks for device ID (leave CRC off for performance reasons)
- `Application` changing USB to 12 Mbit/sec during setup
- Forced mode changes to "tip approach"

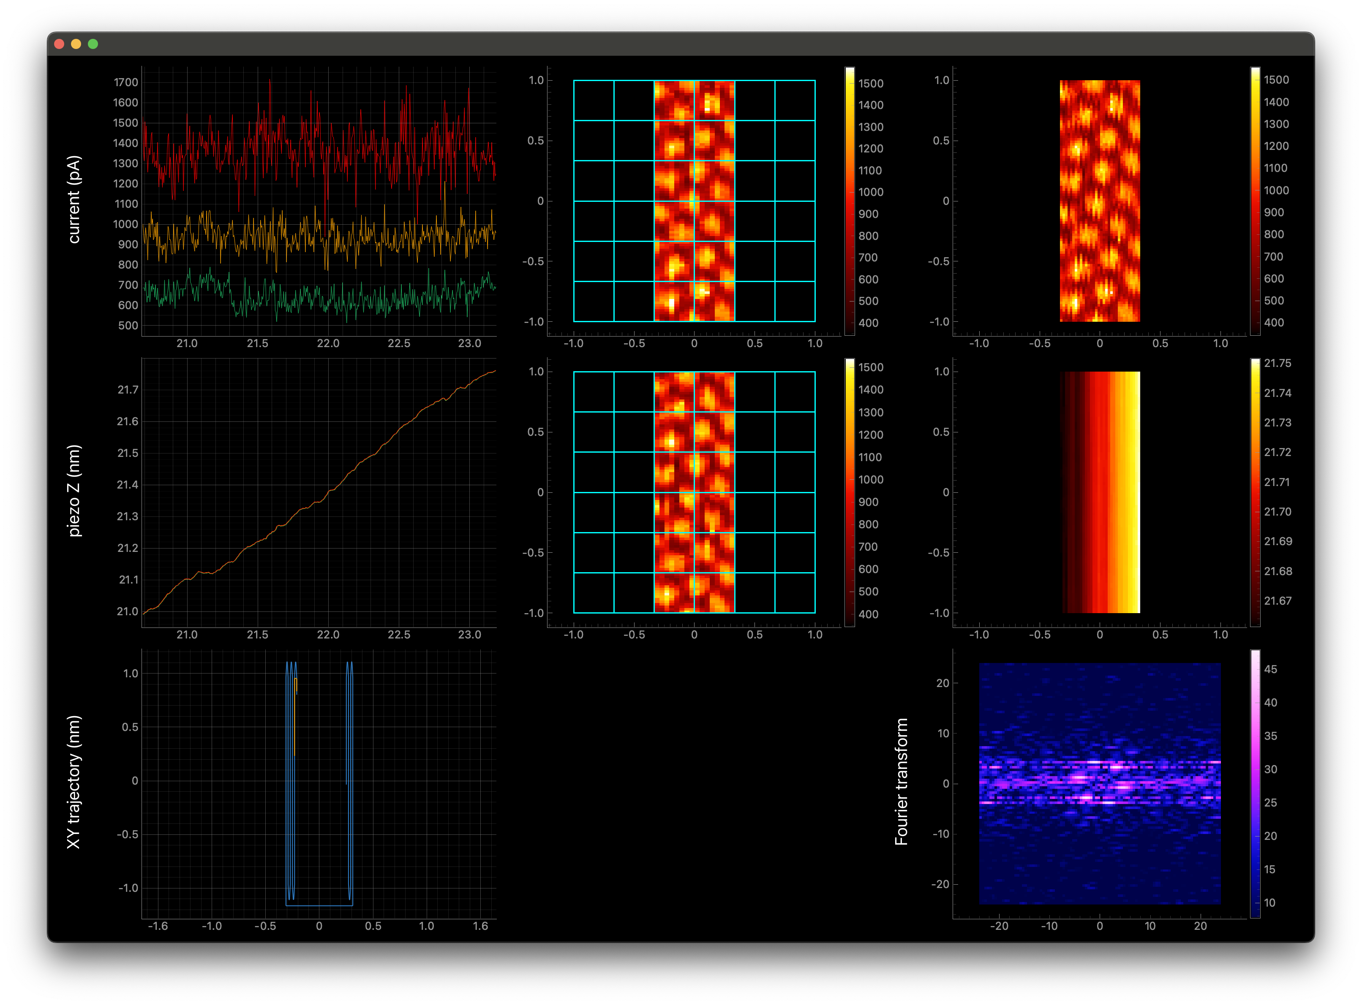
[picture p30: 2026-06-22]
Documentation/June21/Image5_SetElectronicTimeLag150Microseconds.png

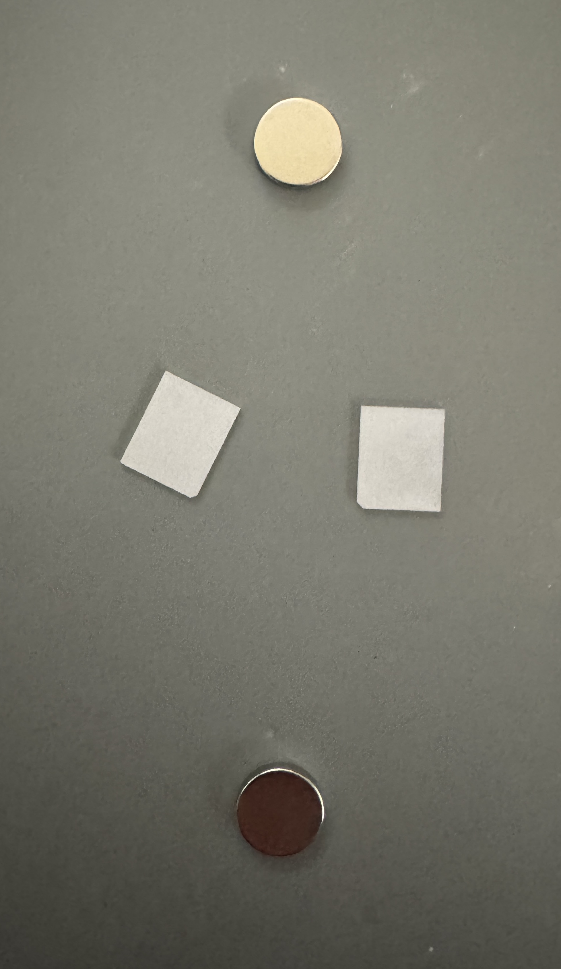
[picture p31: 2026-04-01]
Documentation/March31/March31_Part1.jpg

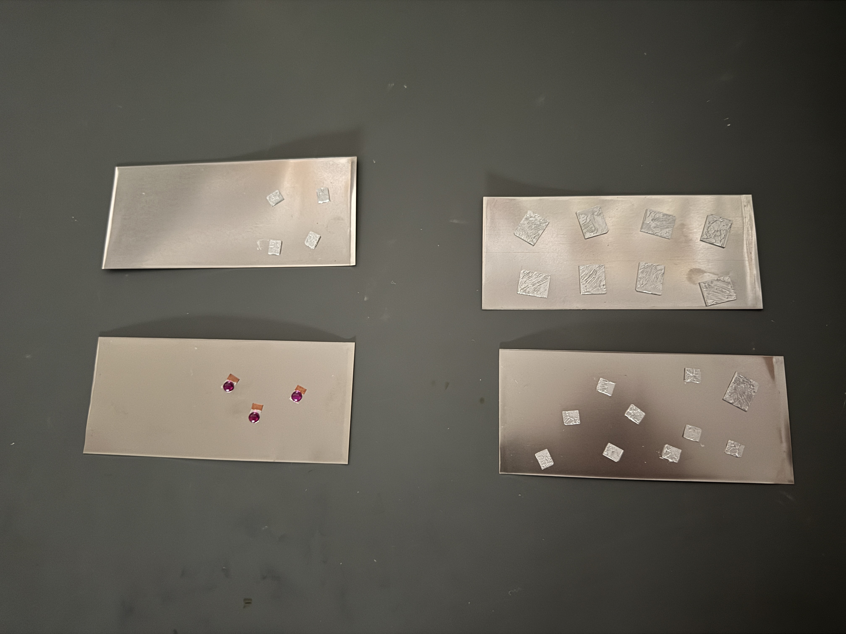
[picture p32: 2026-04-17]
Documentation/April16/April16_Part2.jpg

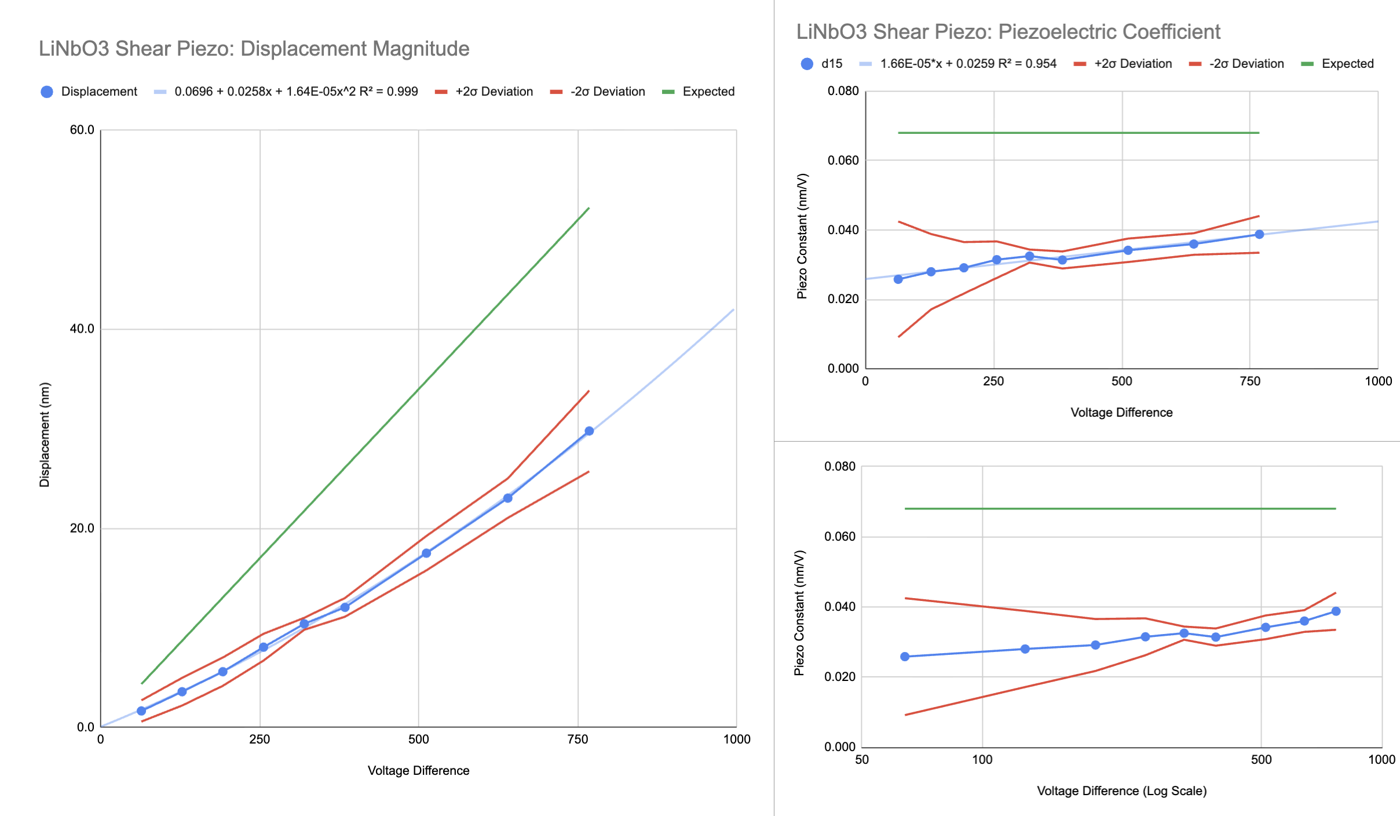
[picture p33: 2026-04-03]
Documentation/April3/April3_Part1.png

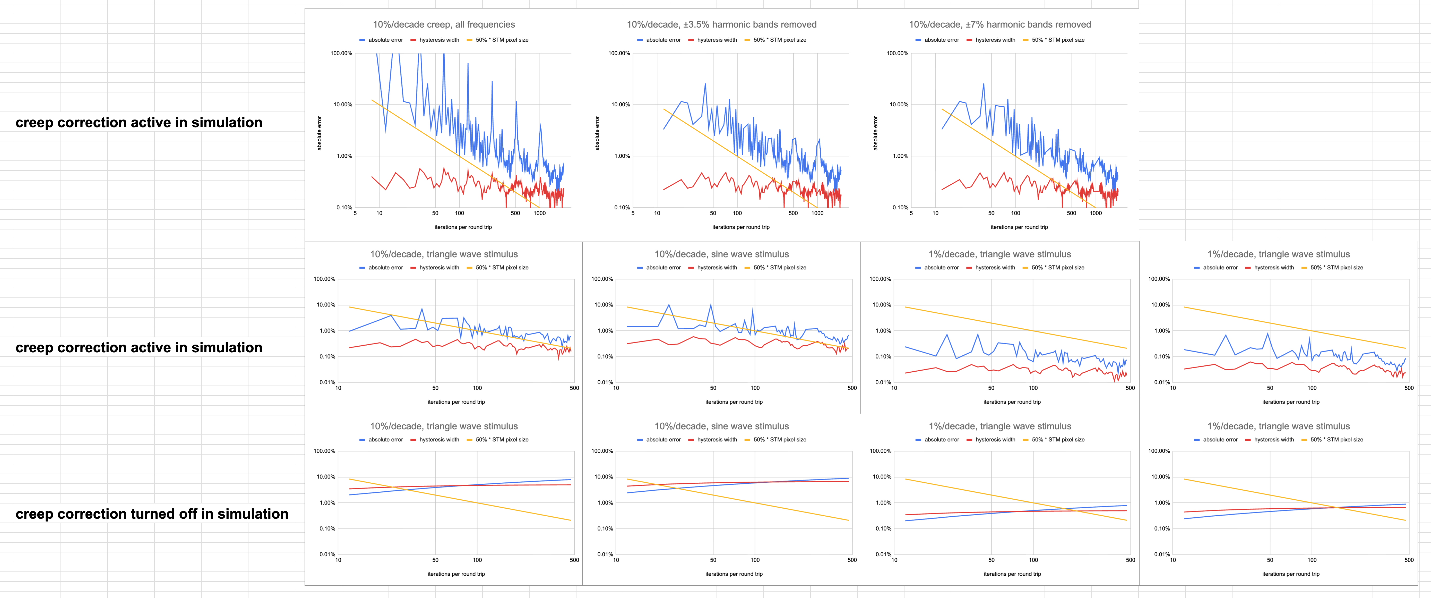
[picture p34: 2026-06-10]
Documentation/June10/June10_Part1.png

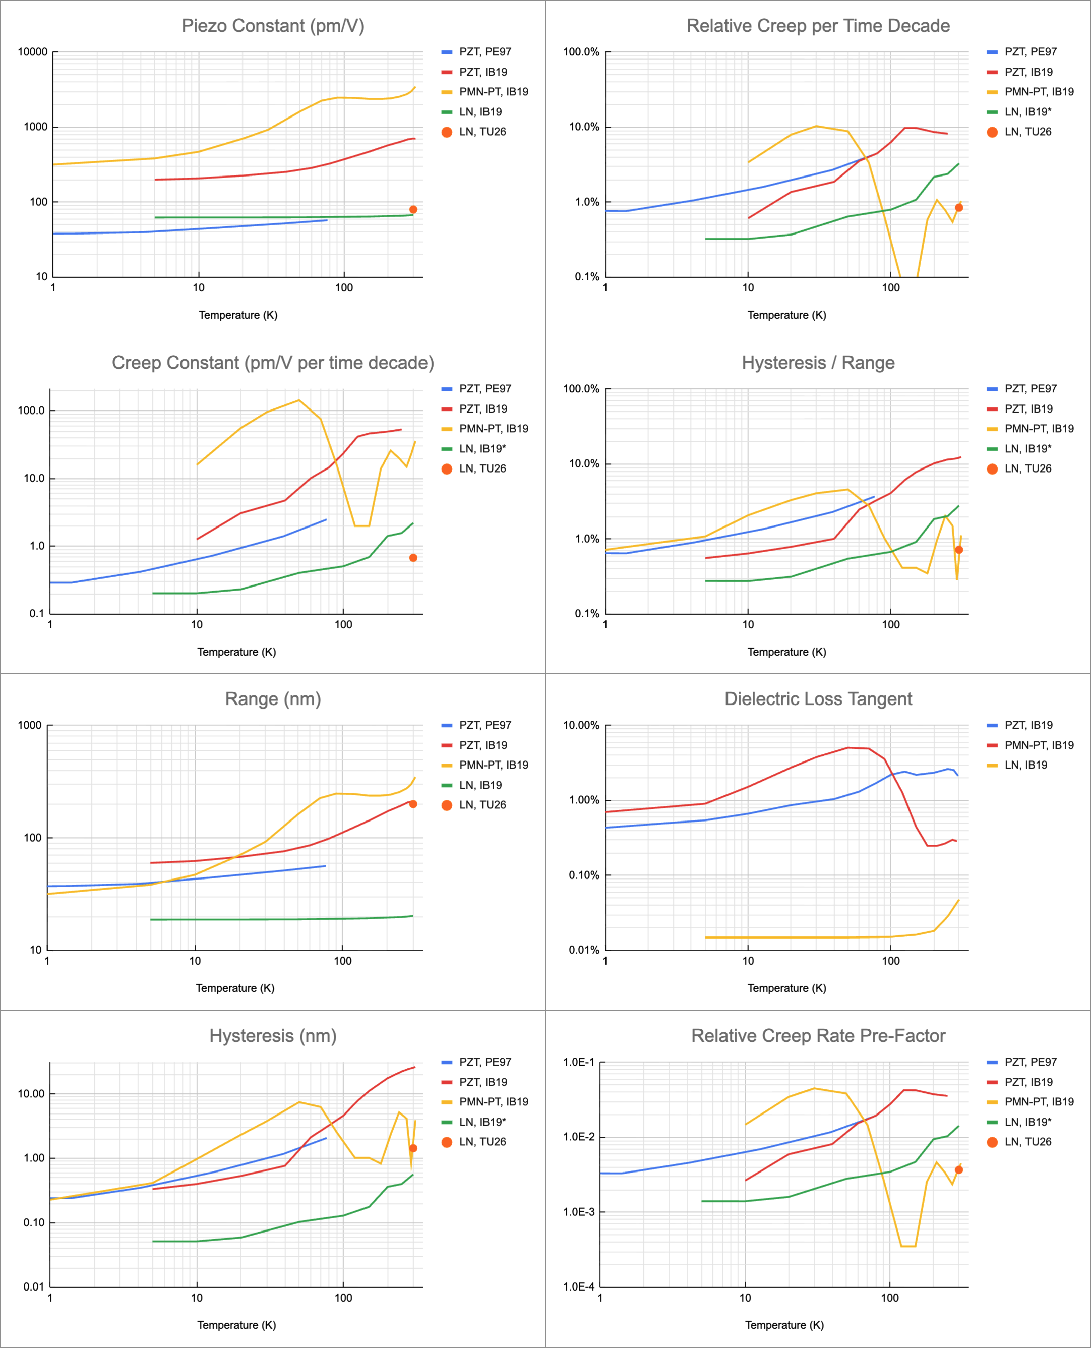
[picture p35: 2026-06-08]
Documentation/June7/June7_Part2.png

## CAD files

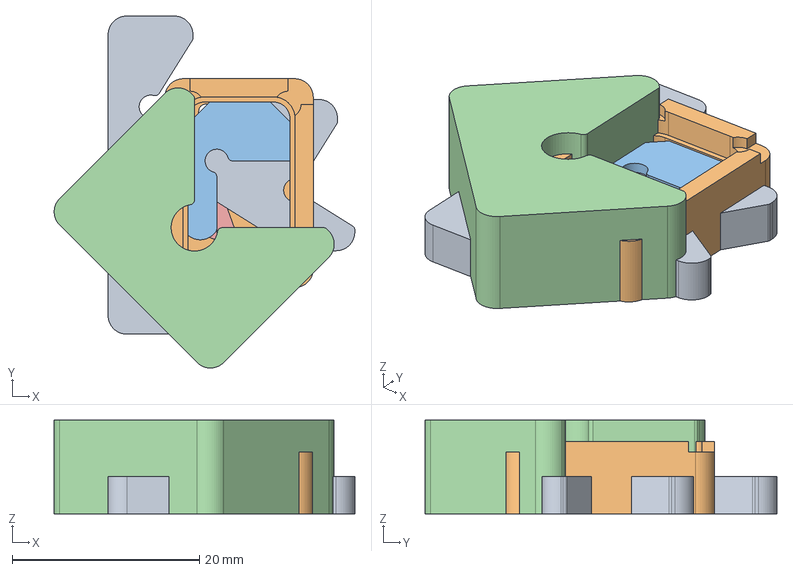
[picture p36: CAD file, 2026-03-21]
Fabrication/3DP/3DP.FCStd
32.1 x 37.6 x 10.0 mm
Kinematic Mount Aligner
PreAmp Shield
Coarse Piezo Aligner 1
Fine Piezo Aligner
Coarse Piezo Aligner 2

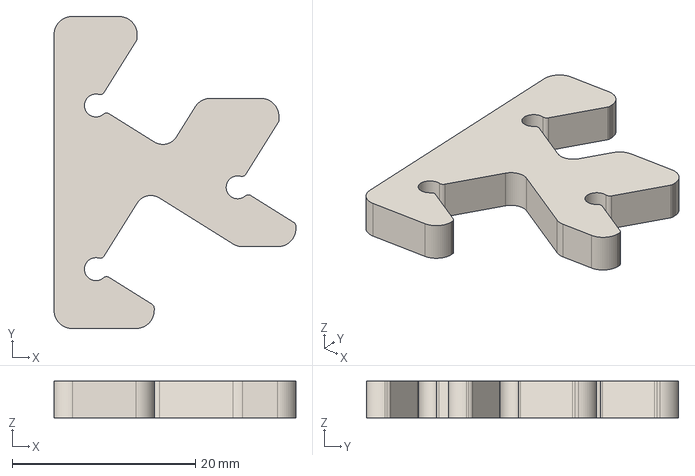
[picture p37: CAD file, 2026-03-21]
Fabrication/3DP/STEP/Kinematic Mount Aligner.step
26.4 x 34.0 x 4.00 mm

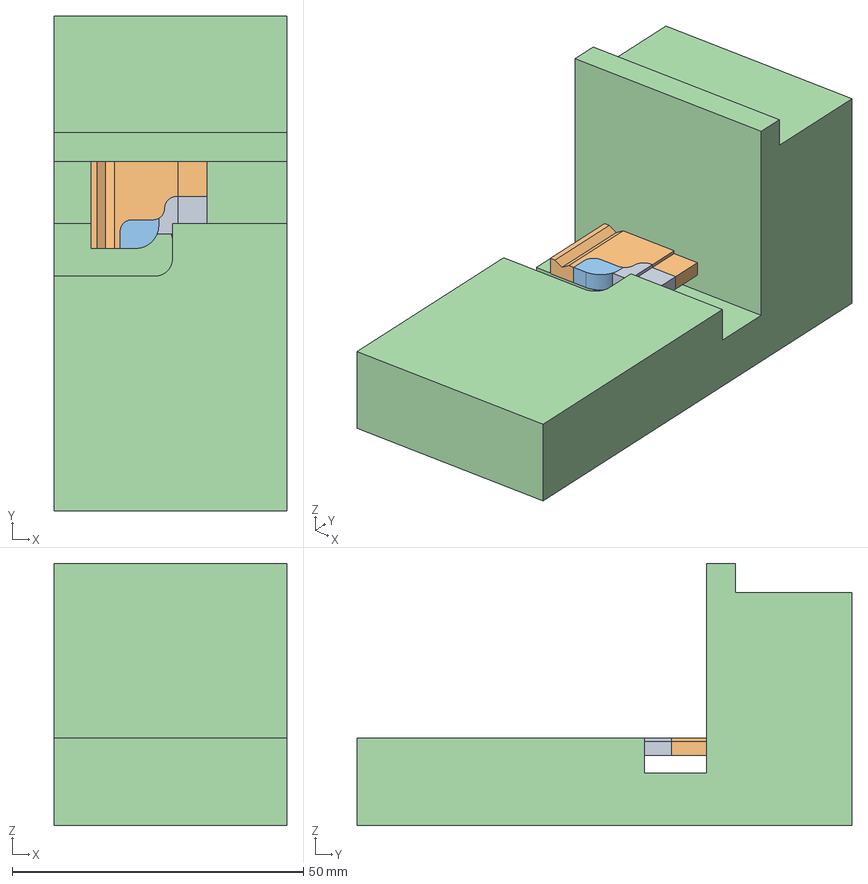
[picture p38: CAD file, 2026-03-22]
Fabrication/CNC/CNC.FCStd
40.0 x 85.0 x 45.0 mm
Coarse Z Slider
Coarse Y Slider
Coarse X Slider
STM Base

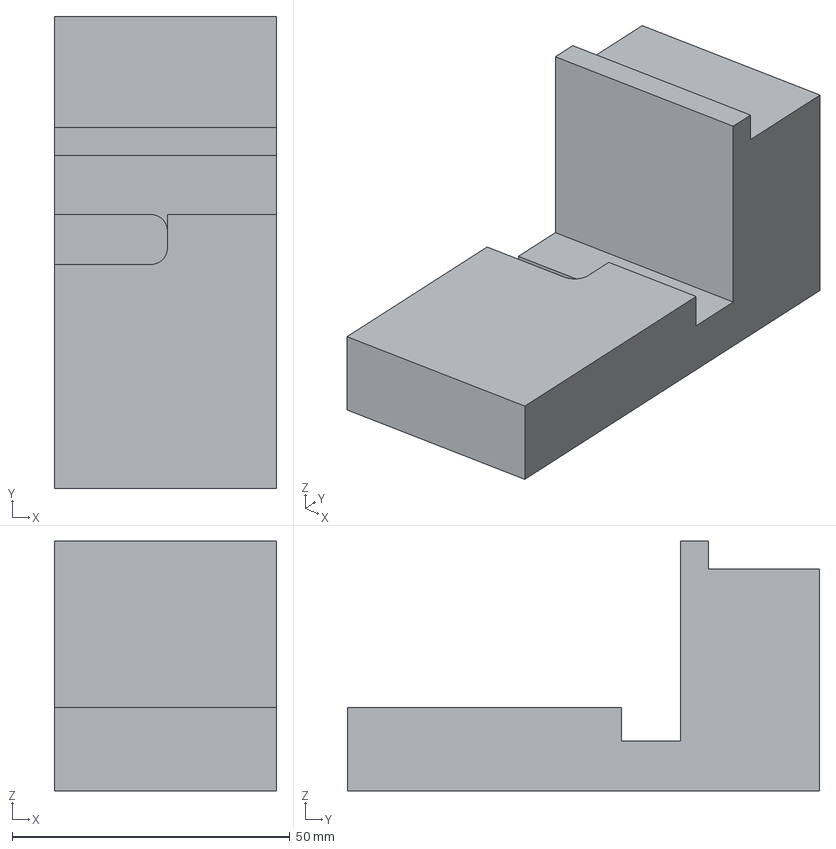
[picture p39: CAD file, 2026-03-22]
Fabrication/CNC/STEP/STM Base.step
40.0 x 85.0 x 45.0 mm

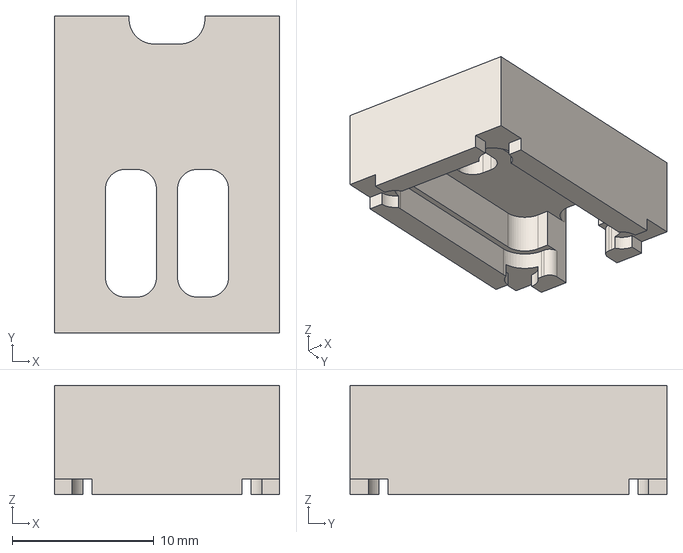
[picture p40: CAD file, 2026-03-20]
Models/CNC/PreAmp Shield.step
15.9 x 22.3 x 7.70 mm

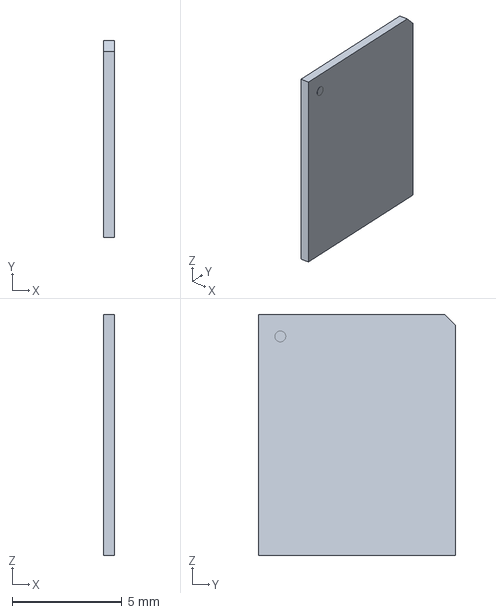
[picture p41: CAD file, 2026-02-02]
Models/LiNbO3_Substrate_Chamfers/v2/LiNbO3_Substrate_10mm.FCStd
0.51 x 9.00 x 11.0 mm

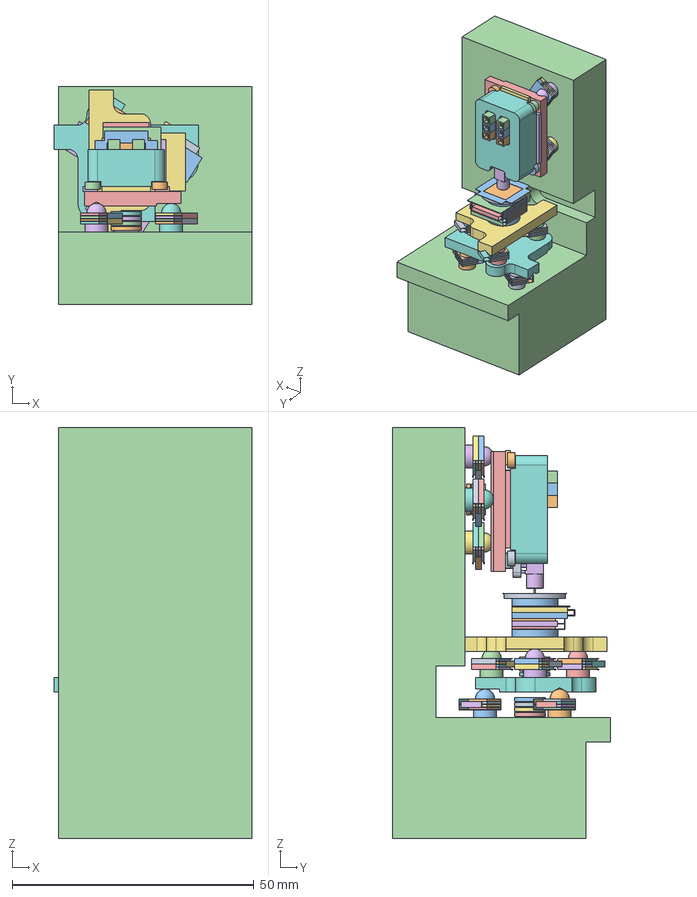
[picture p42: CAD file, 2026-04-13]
Models/PhaseII.FCStd
40.9 x 45.0 x 85.0 mm
Pcb_e57a
NPPC021KFXC-RC_C03 x 2
NPPC021KFXC-RC_C001 x 2
NPPC021KFXC-RC_C002 x 2
Pin - Gold x 2
Pin - Gold001 x 2
Pin - Gold002 x 2
ADP121-AUJZ30R7
ADP121-AUJZ30R001
ADP121-AUJZ30R002
ADP121-AUJZ30R003
ADP121-AUJZ30R004
ADP121-AUJZ30R005
MMCX-J-P-H-RA-SM1_body
H1_Discs2_D21SH_3e0910014654 x 3
PreAmp Shield
KJ_D21SH
KJ_D21SH001
KJ_D21SH002
KJ_D21SH003
Conductive Gasket
Conductive Gasket001
Conductive Gasket002
Conductive Gasket003
Conductive Gasket004
Tungsten Wire
KJ_D61SH
Large Cu Electrode, Short Axis, GND
Large LiNbO3 Plate
Large Cu Electrode, Long Axis, V_X
Large LiNbO3 Plate007
Large Cu Electrode, Short Axis, GND001
Large LiNbO3 Plate009
Large LiNbO3 Plate011
Large Cu Electrode, Short Axis, GND002
Large LiNbO3 Plate013
Large Cu Electrode, Long Axis, V_Y
Large LiNbO3 Plate015
Large Cu Electrode, Short Axis, GND003
Large LiNbO3 Plate017
Large LiNbO3 Plate019
Glass Cover Slip
KJ_D61SH001
Bias Voltage Electrode
Coarse Z Slider
KJ_D31SH005
Small Cu Electrode, Short Axis, GND005
Small LiNbO3 Plate064
Small Cu Electrode001, Long Axis, V005
Small LiNbO3 Plate065
Small Cu Electrode002, Short Axis, GND005
Small LiNbO3 Plate066
Small LiNbO3 Plate067
Sapphire Half-Ball Lens009
KJ_D31SH006
Small Cu Electrode, Short Axis, GND006
Small LiNbO3 Plate068
Small Cu Electrode001, Long Axis, V006
Small LiNbO3 Plate069
Small Cu Electrode002, Short Axis, GND006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

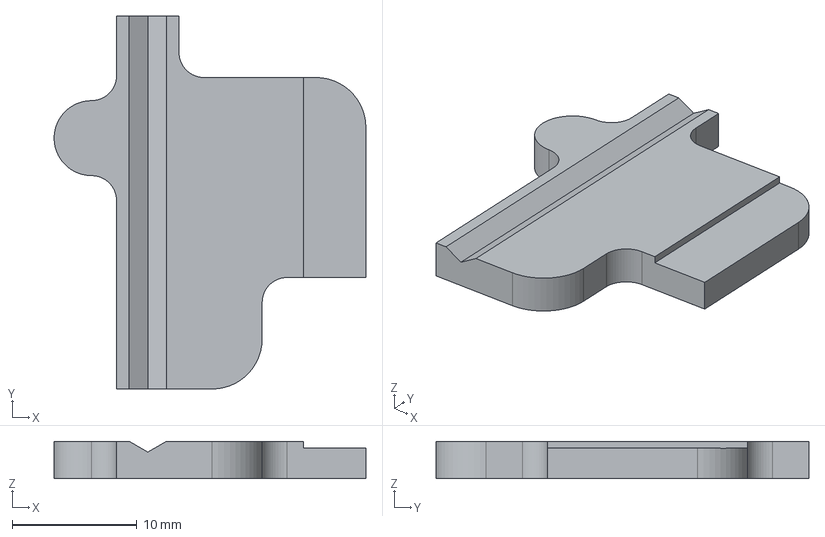
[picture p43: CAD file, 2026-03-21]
Fabrication/CNC/STEP/Coarse X Slider.step
25.0 x 29.8 x 3.00 mm

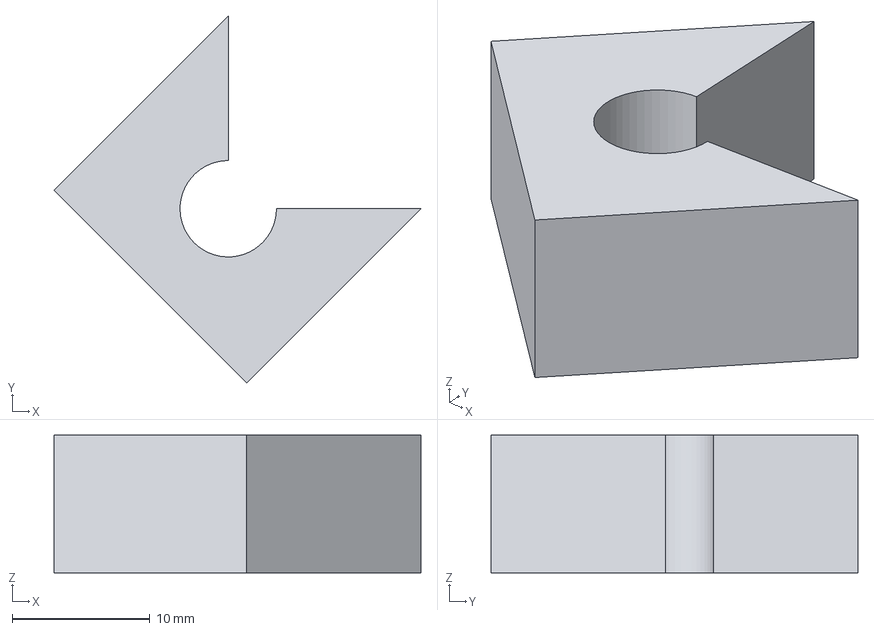
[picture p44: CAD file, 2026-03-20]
Models/CNC/Fine Piezo Aligner.step
26.7 x 26.7 x 10.0 mm

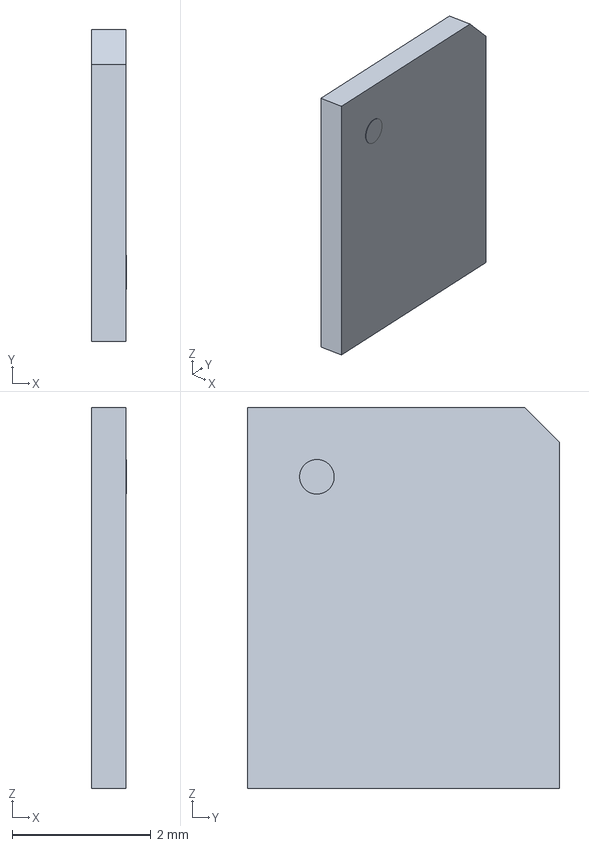
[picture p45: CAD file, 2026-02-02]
Models/LiNbO3_Substrate_Chamfers/v2/LiNbO3_Substrate_5mm.FCStd
0.51 x 4.50 x 5.50 mm

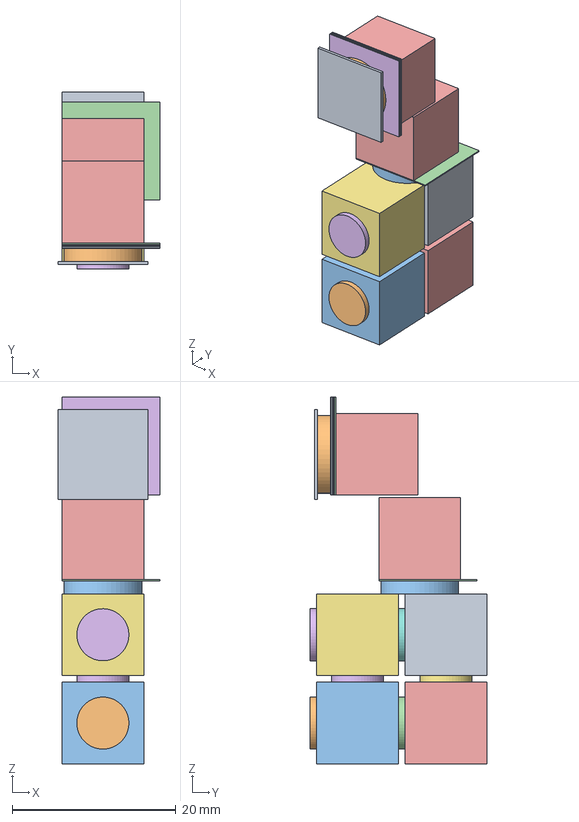
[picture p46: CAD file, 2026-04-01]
Models/PhaseI.FCStd
12.5 x 21.6 x 44.8 mm
Glass Cover Slip002
Glass Cover Slip003
Glass Cover Slip004
Glass Cover Slip005
Steel Cube001
Copper Shim001
Copper Shim
KJ_D31SH017
Copper Shim002
KJ_D61SH002
KJ_D61SH004
Glass Cover Slip007
Copper Cube001
KJ_D401_021
Iron Cube
KJ_D401_022
Iron Cube001
KJ_D401_023
Iron Cube002
KJ_D401_024
Iron Cube003
KJ_D401_025
KJ_D401_026

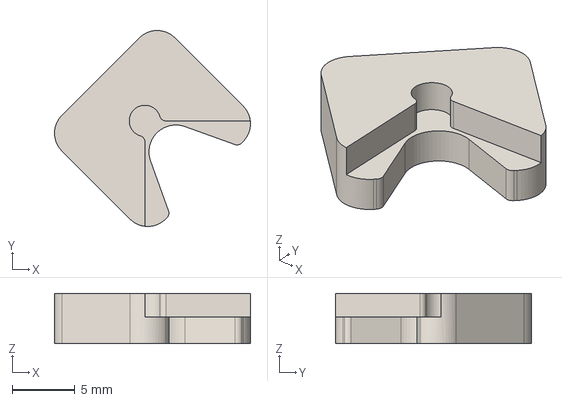
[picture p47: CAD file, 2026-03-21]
Fabrication/3DP/STEP/Coarse Piezo Aligner 2.step
15.7 x 15.7 x 4.00 mm

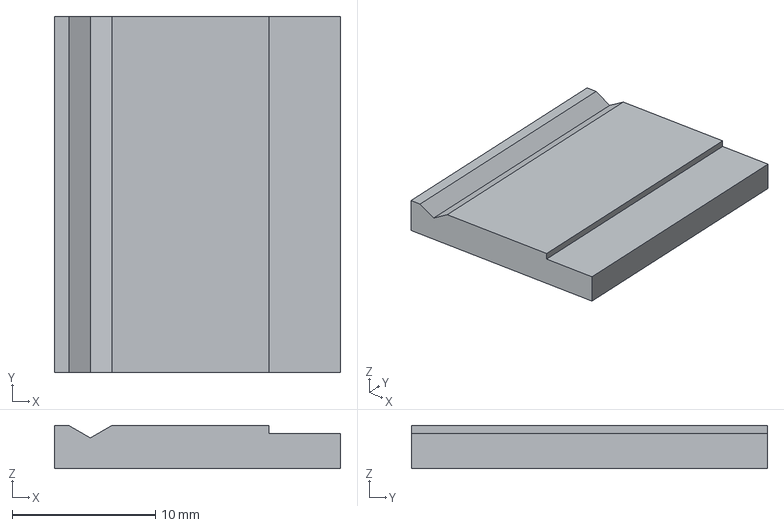
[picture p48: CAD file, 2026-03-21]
Fabrication/CNC/STEP/Coarse Z Slider.step
20.0 x 24.8 x 3.00 mm

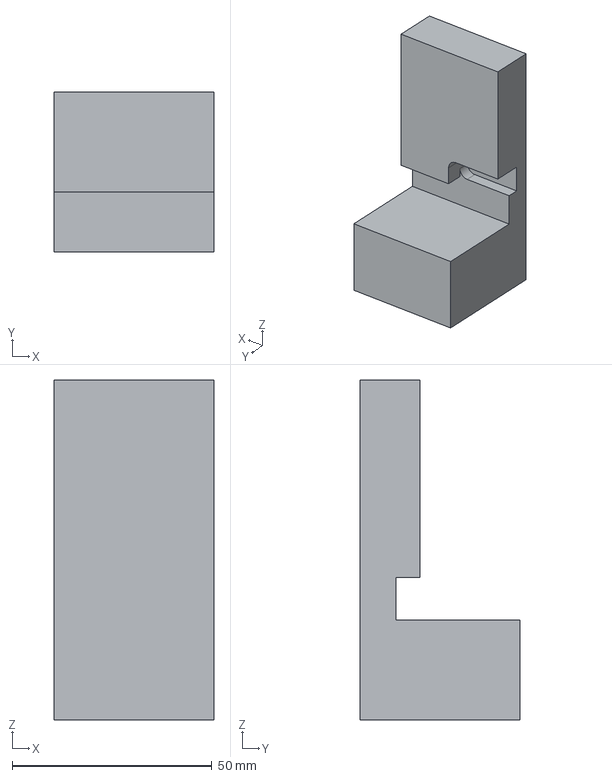
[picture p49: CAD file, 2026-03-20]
Models/CNC/STM Base.step
40.0 x 40.0 x 85.0 mm

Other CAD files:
Fabrication/3DP/STEP/PreAmp Shield.step
Models/KiCadStepUp.FCStd
Fabrication/3DP/STEP/Fine Piezo Aligner.step
Fabrication/CNC/STEP/Coarse Y Slider.step
Fabrication/3DP/STEP/Coarse Piezo Aligner 1.step
Models/CNC/Coarse Piezo Aligner 1.step
Models/CNC/Coarse Piezo Aligner 2.step
Models/CNC/Coarse X Slider.step
Models/CNC/Coarse Y Slider.step
Models/CNC/Coarse Z Slider.step
Models/CNC/Kinematic Mount Aligner.step
Models/LabSpace.FCStd
Models/LiNbO3_Substrate_Chamfers/v1/LiNbO3_Substrate_10mm.FCStd
Models/LiNbO3_Substrate_Chamfers/v1/LiNbO3_Substrate_5mm.FCStd

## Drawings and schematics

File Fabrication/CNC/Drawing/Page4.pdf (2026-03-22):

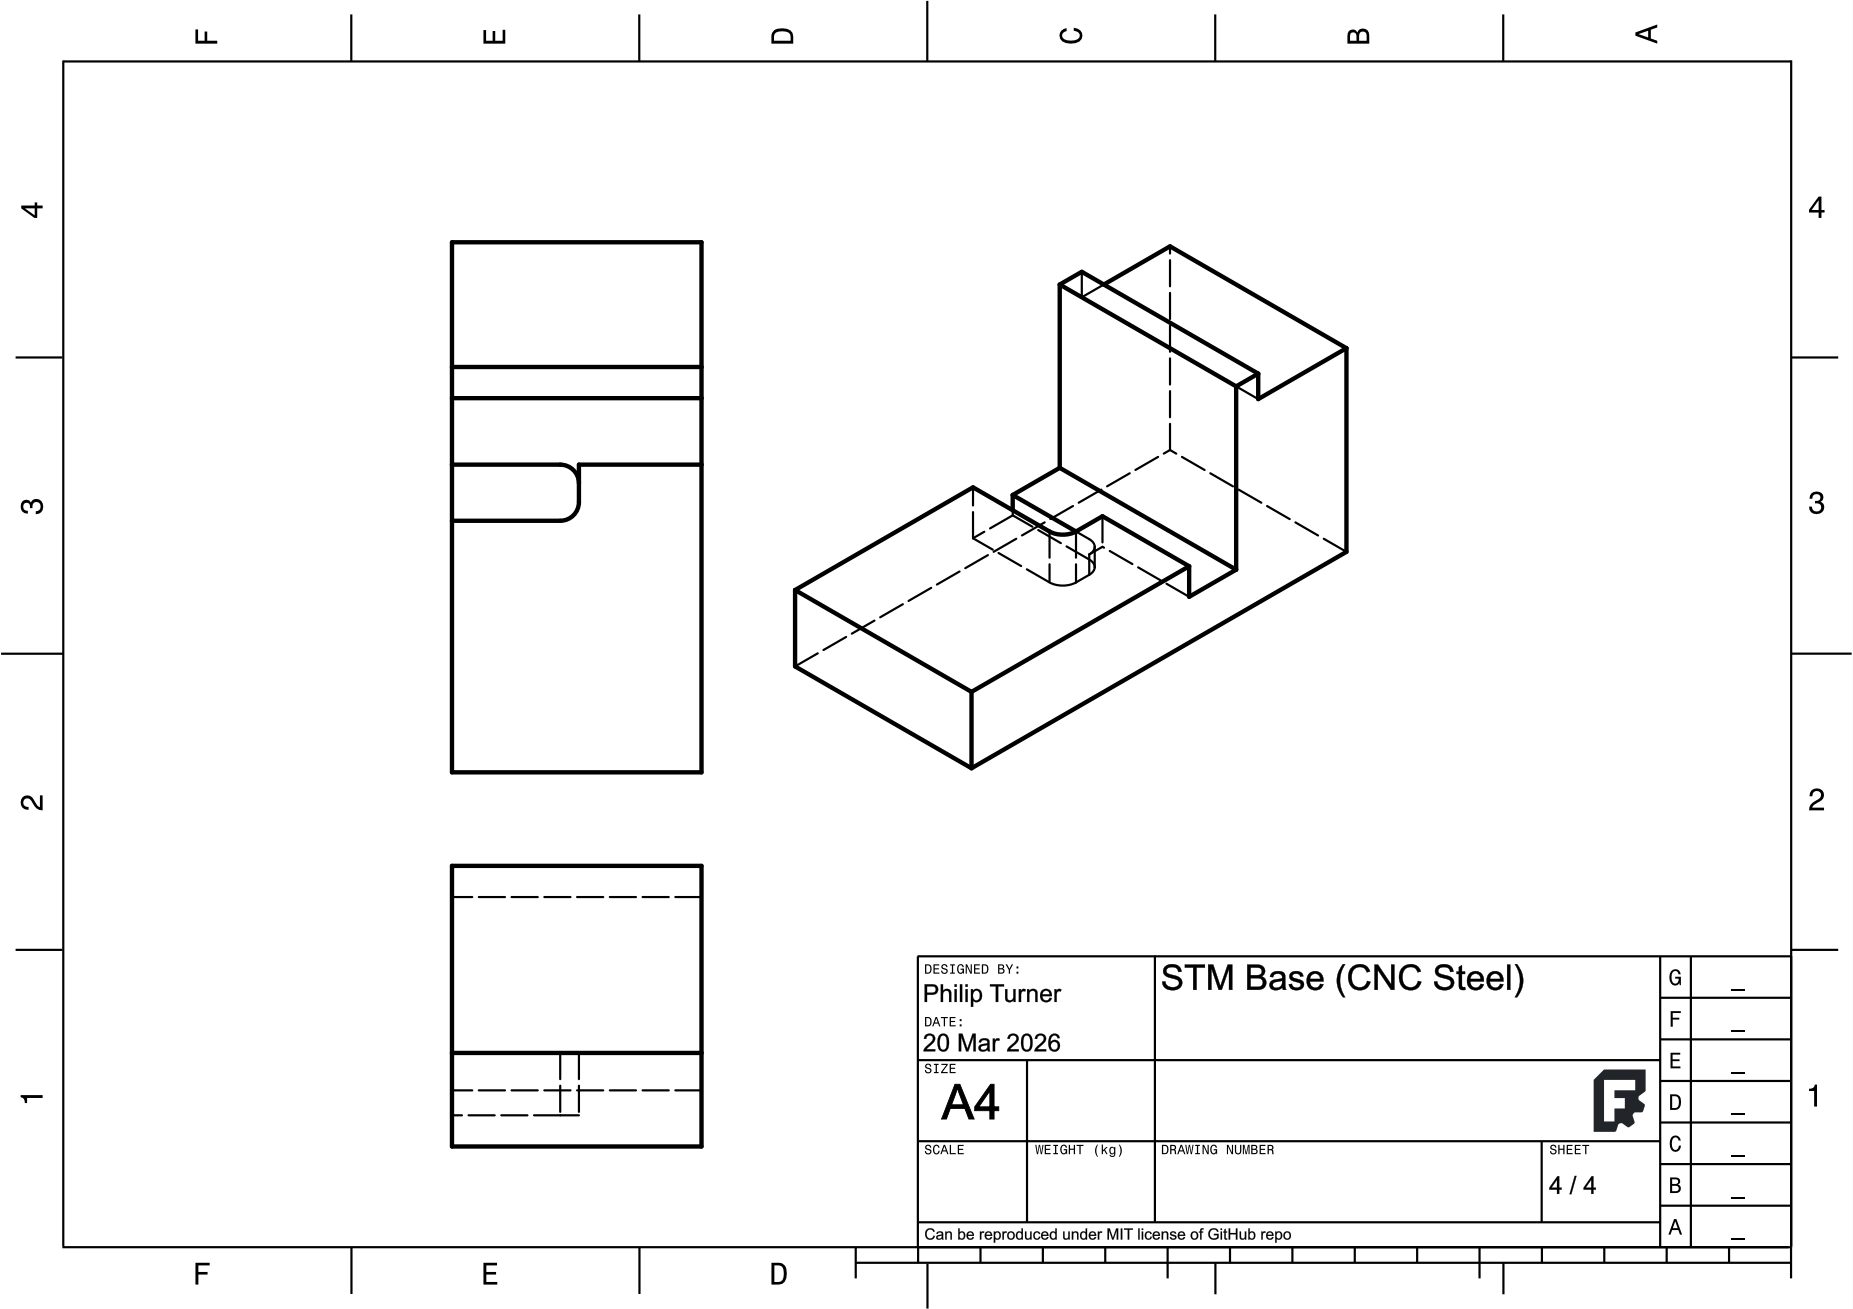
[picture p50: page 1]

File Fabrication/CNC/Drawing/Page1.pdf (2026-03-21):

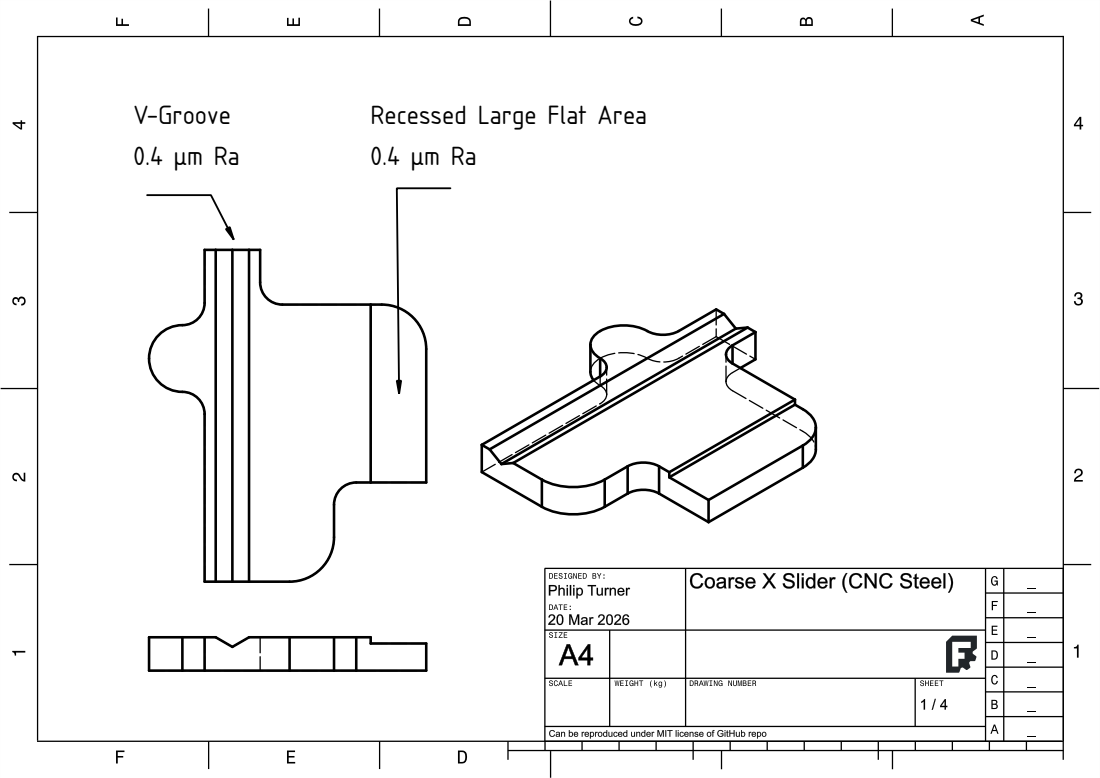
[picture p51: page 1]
Flat Are

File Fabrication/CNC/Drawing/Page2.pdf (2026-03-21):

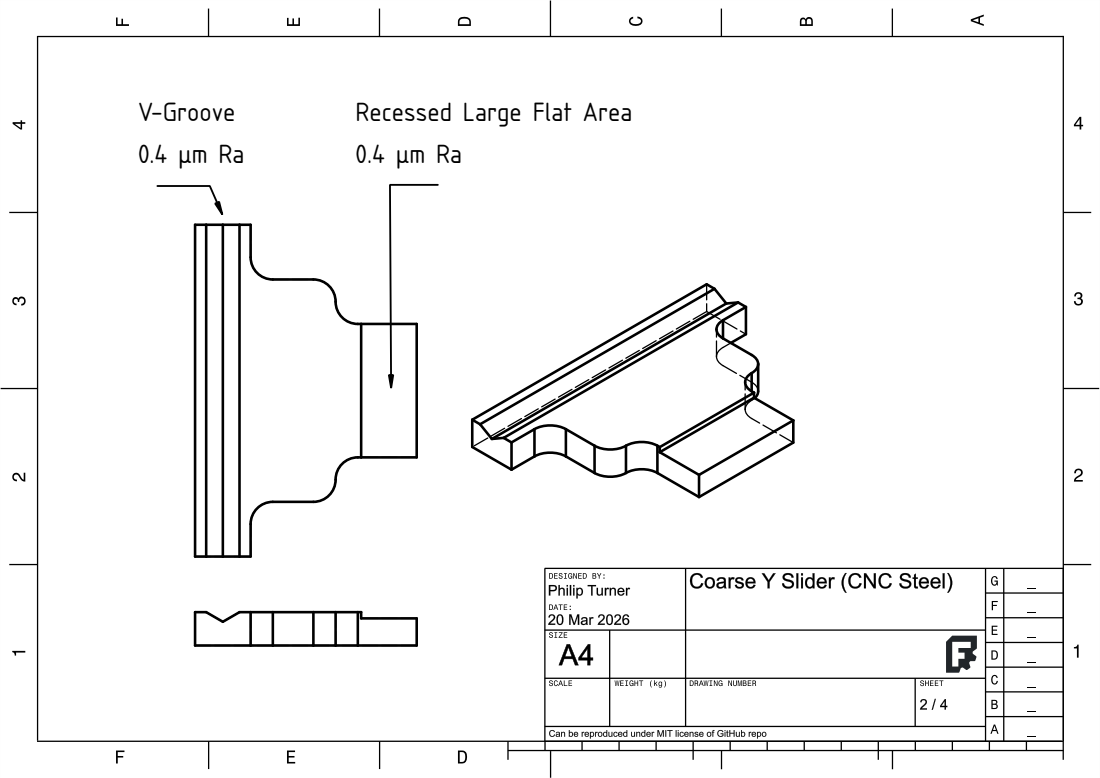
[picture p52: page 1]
Flat Are

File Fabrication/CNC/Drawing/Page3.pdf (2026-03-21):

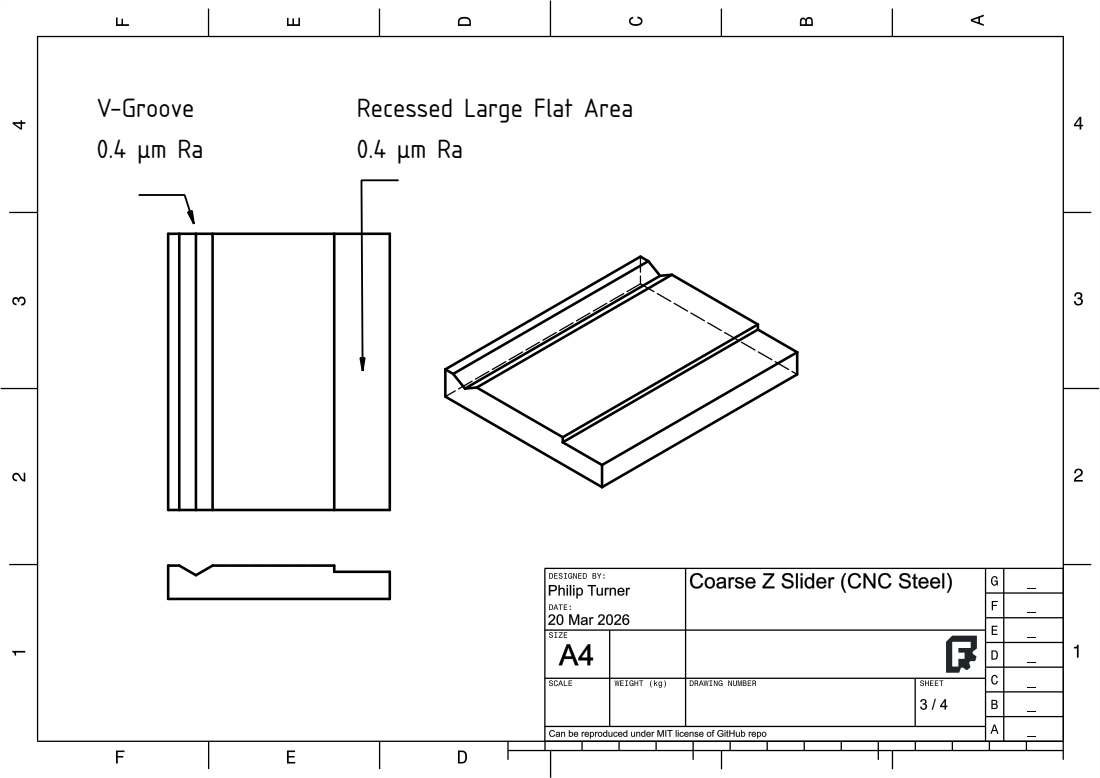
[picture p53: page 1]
Flat Are

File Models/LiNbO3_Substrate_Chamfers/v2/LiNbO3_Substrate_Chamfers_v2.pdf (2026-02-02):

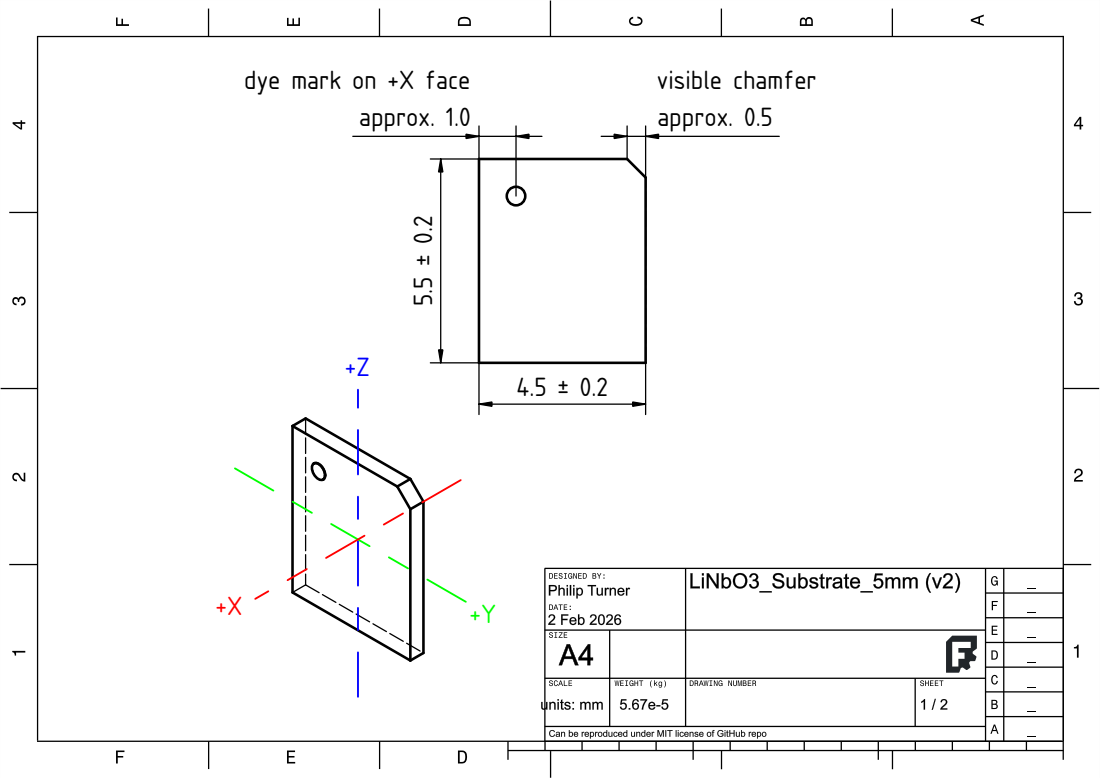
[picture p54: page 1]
approx. 1.0; approx. 0.5; dye mark on +X face; visible chamfer

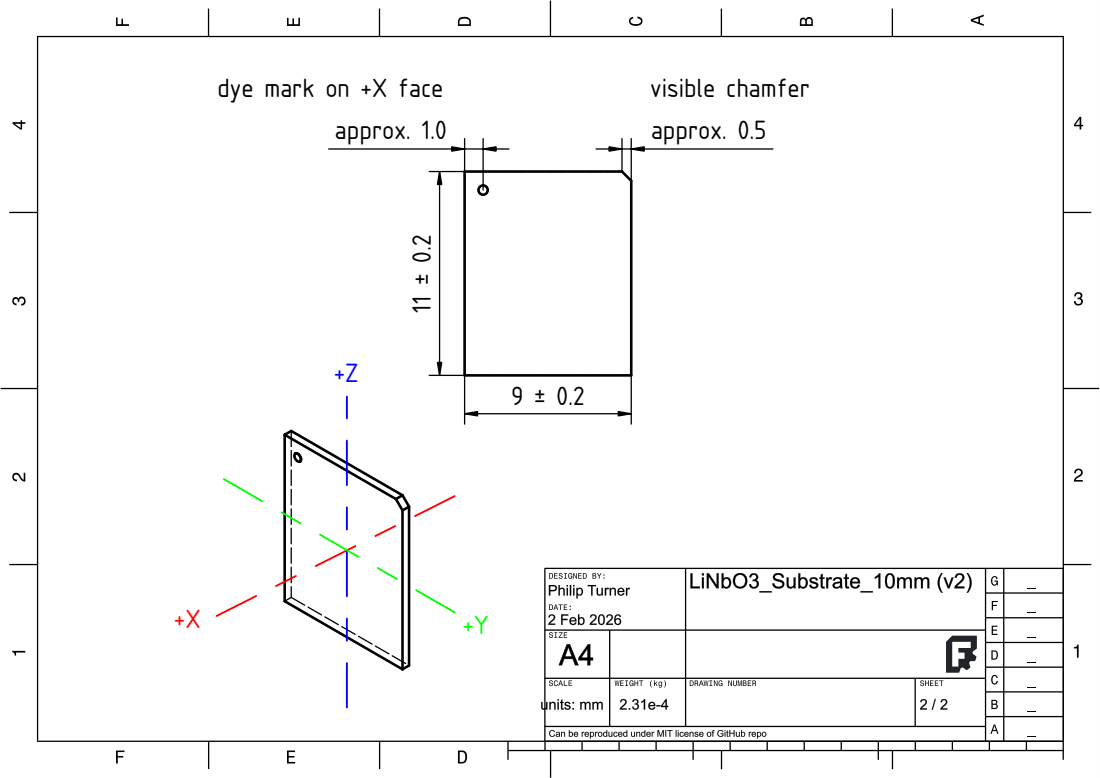
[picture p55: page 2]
approx. 1.0; approx. 0.5; dye mark on +X face; visible chamfer

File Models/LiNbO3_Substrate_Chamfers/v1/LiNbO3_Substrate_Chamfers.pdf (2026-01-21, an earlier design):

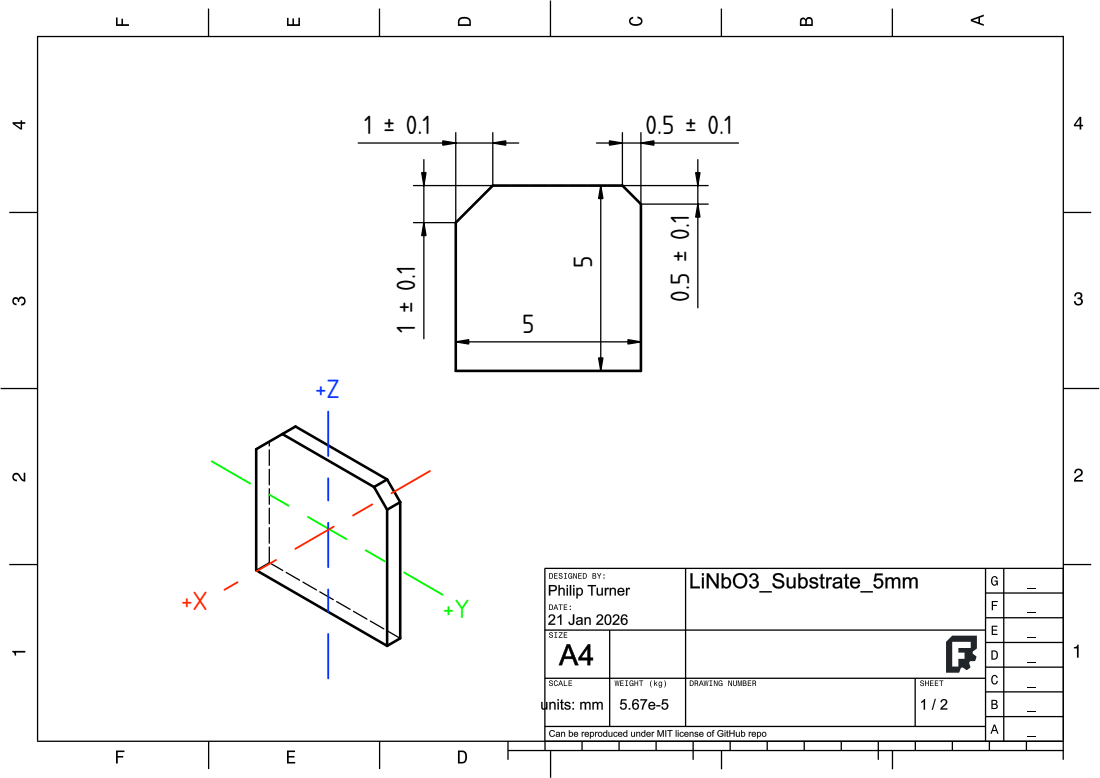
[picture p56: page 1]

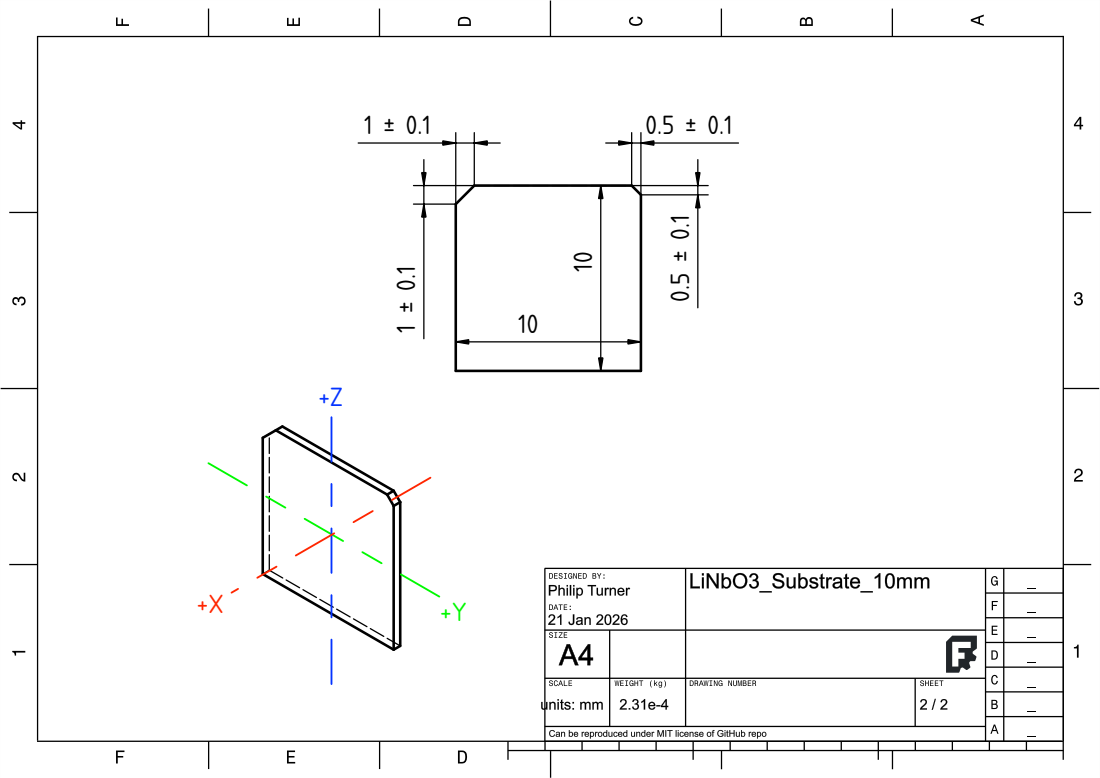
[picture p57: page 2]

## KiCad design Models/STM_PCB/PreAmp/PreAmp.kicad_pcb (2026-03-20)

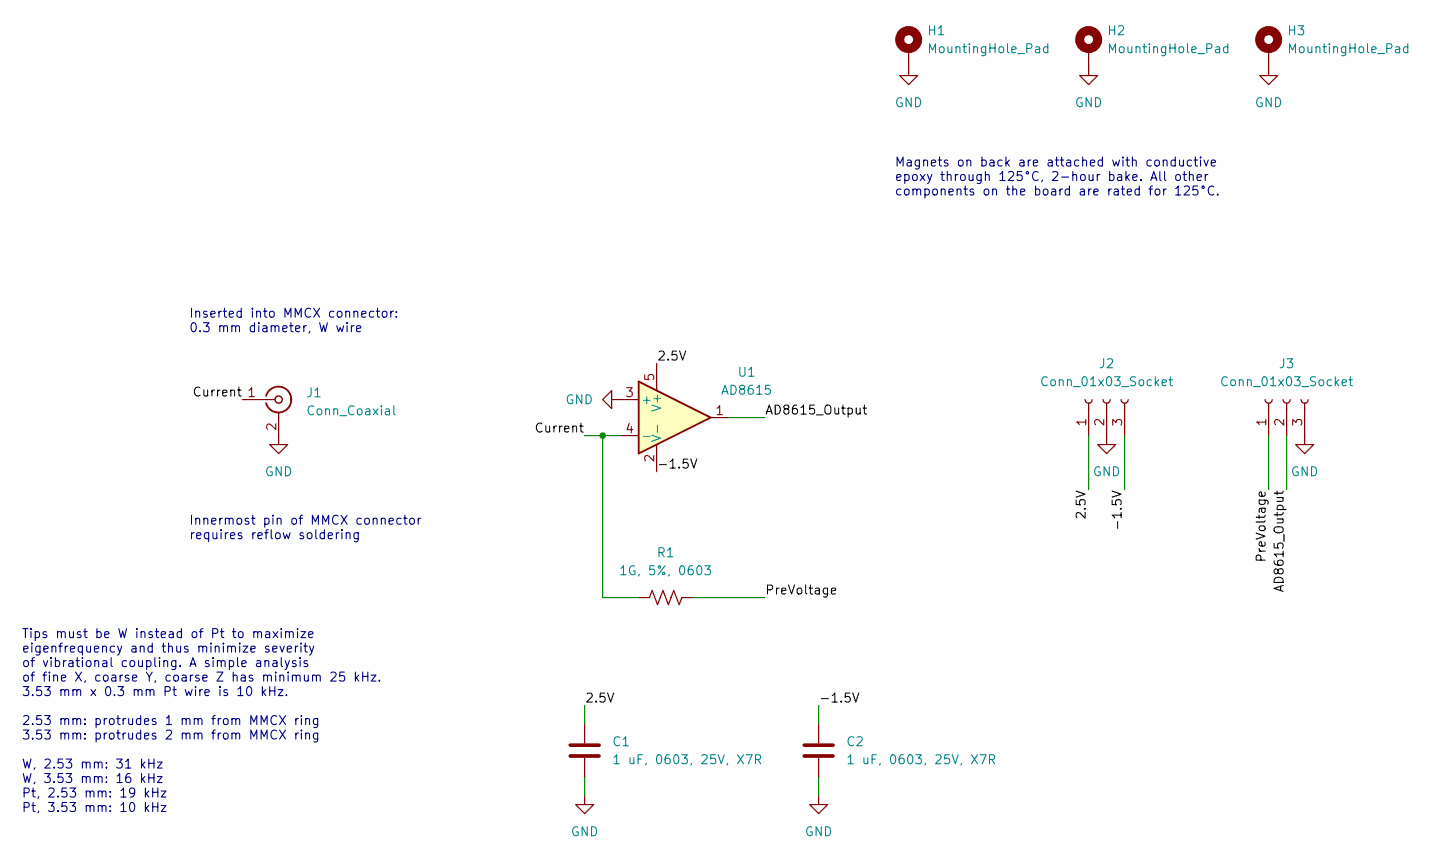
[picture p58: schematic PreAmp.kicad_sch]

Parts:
C1, C2: 1 uF, 0603, 25V, X7R; CAPC0603
H1, H2, H3: MountingHole_Pad; KJ_D21SH
J1: Conn_Coaxial; Samtec_MMCX_SMT
J2, J3: Conn_01x03_Socket; PinSocket_1x3_SMT
R1: 1G, 5%, 0603; RESC0603
U1: AD8615

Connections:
/2.5V: C1.1, J2.1, U1.5 (V+)
/-1.5V: C2.1, J2.3, U1.2 (V-)
/AD8615_Output: J3.2, U1.1
/Current: J1.1 (In), R1.1, U1.4 (-)
/PreVoltage: J3.1, R1.2
GND: C1.2, C2.2, H1.1, H2.1, H3.1, J1.2 (Ext), J2.2, J3.3, U1.3 (+)

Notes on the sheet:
Tips must be W instead of Pt to maximize eigenfrequency and thus minimize severity of vibrational coupling. A simple analysis of fine X, coarse Y, coarse Z has minimum 25 kHz. 3.53 mm x 0.3 mm Pt wire is 10 kHz. 2.53 mm: protrudes 1 mm from MMCX ring 3.53 mm: protrudes 2 mm from MMCX ring W, 2.53 m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
Inserted into MMCX connector: 0.3 mm diameter, W wire
Magnets on back are attached with conductive epoxy through 125°C, 2-hour bake. All other components on the board are rated for 125°C.
Innermost pin of MMCX connector requires reflow soldering

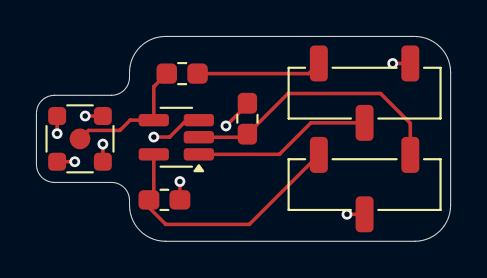
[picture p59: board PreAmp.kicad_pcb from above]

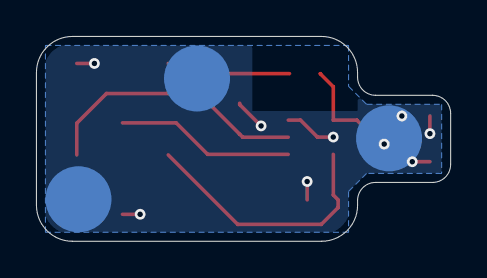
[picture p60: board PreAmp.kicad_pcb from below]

Board: 2 copper layers, 23.0 x 11.4 mm, 10 parts (3 on the bottom side), 6 nets.

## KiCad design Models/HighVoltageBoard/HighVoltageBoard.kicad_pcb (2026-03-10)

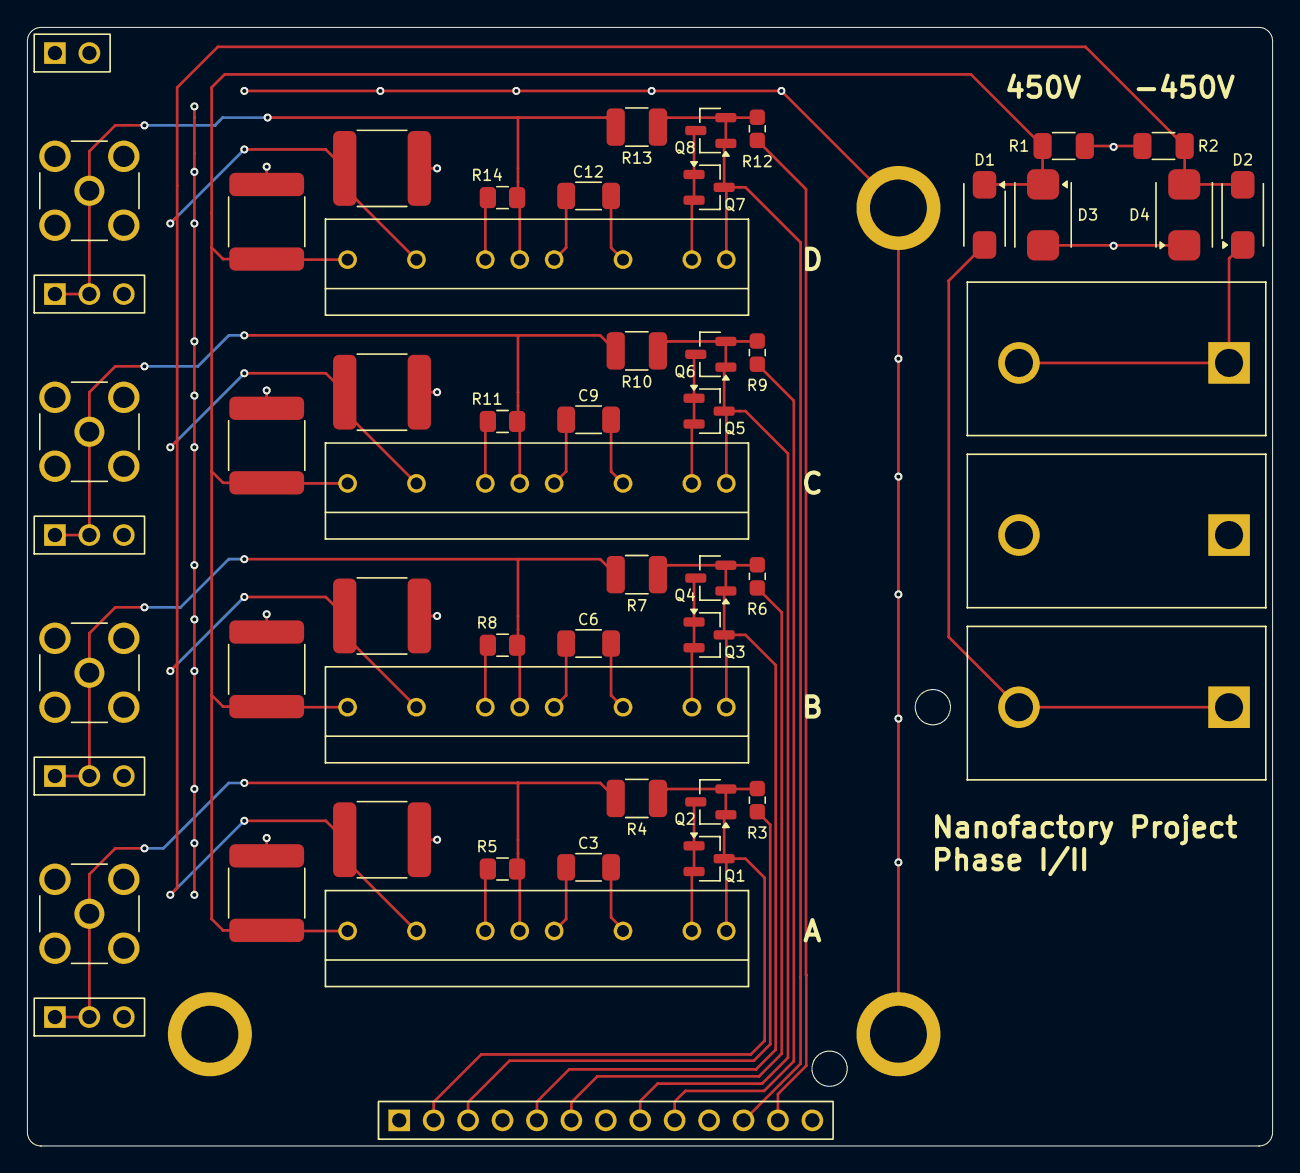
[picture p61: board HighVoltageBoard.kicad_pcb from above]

Board: 2 copper layers, 91.9 x 82.5 mm, 68 parts (0 on the bottom side), 37 nets.

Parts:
C1, C2, C4, C5, C7, C8, C10, C11: 47 nF, 630V; CAPC2220_GRJ
C3, C6, C9, C12: 10 pF, 1 kV; CAPC1206_CHV
D1, D2: Vr = 2 kV; DO-214AC
D3, D4: Vr = 451V; DO-214AA
H1, H2, H4: Mounting Hole, M2.5; Keystone_24929
H3, H5: Dowel Pin, M2.5; DowelPin_2.5mm
J1: Conn_01x13_Socket; PinSocket_1x13
J2: Conn_01x02_Pin; PinHeader_1x2
J3: Banana Socket, Green; Multicomp_24.243
J4: Banana Socket, Black; Multicomp_24.243
J5: Banana Socket, Blue; Multicomp_24.243
J6, J9, J12, J15: Conn_Coaxial; RFPC-SMA27-F
J7, J10, J13, J16: Conn_01x03_Pin; PinHeader_1x3
NT1, NT3, NT5, NT7: NetTie_2; NetTie_0.2mm_HighVoltage
NT2, NT4, NT6, NT8: NetTie_2; NetTie_0.2mm
Q1, Q2, Q3, Q4, Q5, Q6, Q7, Q8: Q_NJFET_DSG; SOT-23
R1, R2: 1M, 5%, 0.33W, 800V; RESC1206_RCV
R3, R6, R9, R12: 28k, 0.1%; RESC0603
R4, R7, R10, R13: 1M, 0.1%, 0.33W, 1 kV; RESC1210_TNPV
R5, R8, R11, R14: 15, 1%, 0.25W, 1.9V; RESC0805
U1, U2, U3, U4: PA95

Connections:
450V: C1.1, C4.1, C7.1, C10.1, D1.1 (K), D3.1 (K), R1.1, U1.12 (+VS), U2.12 (+VS), U3.12 (+VS), U4.12 (+VS)
-450V: C2.1, C5.1, C8.1, C11.1, D2.2 (A), D4.2 (A), R2.2, U1.10 (-VS), U2.10 (-VS), U3.10 (-VS), U4.10 (-VS)
/AmplifierA/-IN: NT2.1, Q1.3 (G), Q2.1 (D), Q2.2 (S), R3.2, R4.1, U1.1 (-IN)
/AmplifierA/CC_1: C3.1, U1.4 (CC_1)
/AmplifierA/CC_2: C3.2, U1.6 (CC_2)
/AmplifierB/-IN: NT4.1, Q3.3 (G), Q4.1 (D), Q4.2 (S), R6.2, R7.1, U2.1 (-IN)
/AmplifierB/CC_1: C6.1, U2.4 (CC_1)
/AmplifierB/CC_2: C6.2, U2.6 (CC_2)
/AmplifierC/-IN: NT6.1, Q5.3 (G), Q6.1 (D), Q6.2 (S), R9.2, R10.1, U3.1 (-IN)
/AmplifierC/CC_1: C9.1, U3.4 (CC_1)
/AmplifierC/CC_2: C9.2, U3.6 (CC_2)
/AmplifierD/-IN: NT8.1, Q7.3 (G), Q8.1 (D), Q8.2 (S), R12.2, R13.1, U4.1 (-IN)
/AmplifierD/CC_1: C12.1, U4.4 (CC_1)
/AmplifierD/CC_2: C12.2, U4.6 (CC_2)
/INA: J1.3, R3.1
/INB: J1.6, R6.1
/INC: J1.9, R9.1
/IND: J1.12, R12.1
/OUTA: J6.1 (In), J7.1, J7.2, NT1.1, R4.2
/OUTB: J9.1 (In), J10.1, J10.2, NT3.1, R7.2
/OUTC: J12.1 (In), J13.1, J13.2, NT5.1, R10.2
/OUTD: J15.1 (In), J16.1, J16.2, NT7.1, R13.2
/SENSENA: J1.2, NT2.2
/SENSENB: J1.5, NT4.2
/SENSENC: J1.8, NT6.2
/SENSEND: J1.11, NT8.2
/WallPower/450V_PreDiode: D1.2 (A), J3.1, J3.2
/WallPower/-450V_PreDiode: D2.1 (K), J5.1, J5.2
GND: C1.2, C2.2, C4.2, C5.2, C7.2, C8.2, C10.2, C11.2, D3.2 (A), D4.1 (K), H1.1, H2.1, H4.1, J1.1, J1.4, J1.7, J1.10, J1.13, J2.1, J2.2, J4.1, J4.2, J6.2 (Ext), J7.3, J9.2 (Ext), J10.3, J12.2 (Ext), J13.3, J15.2 (Ext), J16.3, Q1.1 (D), Q1.2 (S), Q2.3 (G), Q3.1 (D), Q3.2 (S), Q4.3 (G), Q5.1 (D), Q5.2 (S), Q6.3 (G), Q7.1 (D), Q7.2 (S), Q8.3 (G), R1.2, R2.1, U1.2 (+IN), U2.2 (+IN), U3.2 (+IN), U4.2 (+IN)
unnamed: R5.1, U1.8 (CL)
unnamed: NT1.2, R5.2, U1.7 (OUT)
unnamed: R8.1, U2.8 (CL)
unnamed: NT3.2, R8.2, U2.7 (OUT)
unnamed: R11.1, U3.8 (CL)
unnamed: NT5.2, R11.2, U3.7 (OUT)
unnamed: R14.1, U4.8 (CL)
unnamed: NT7.2, R14.2, U4.7 (OUT)

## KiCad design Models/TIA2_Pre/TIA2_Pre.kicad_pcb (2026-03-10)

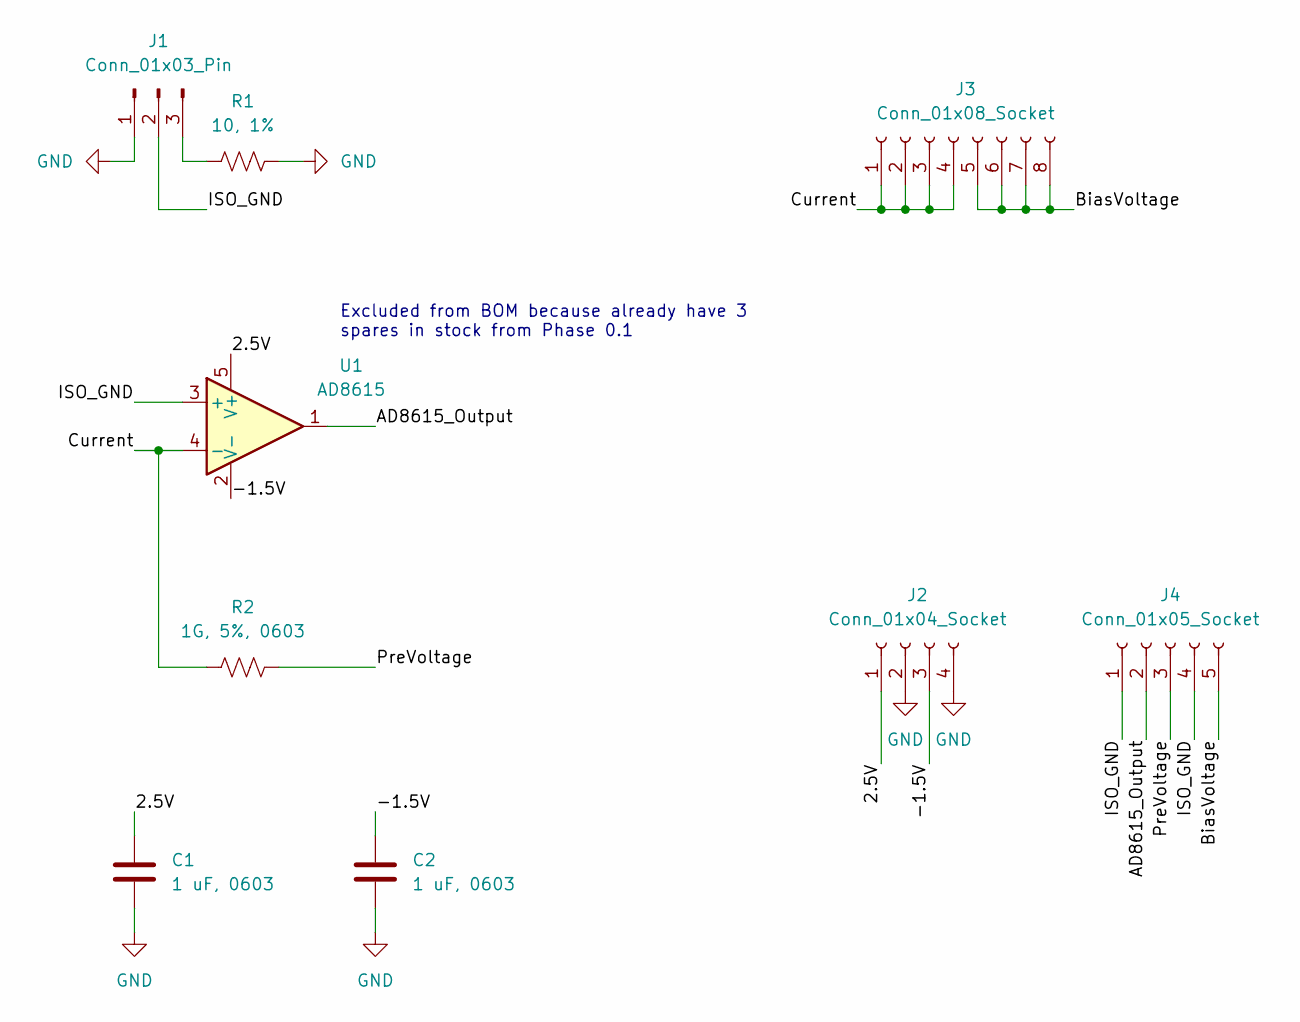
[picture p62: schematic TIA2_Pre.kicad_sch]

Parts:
C1, C2: 1 uF, 0603; CAPC0603
J1: Conn_01x03_Pin; PinHeader_1x3
J2: Conn_01x04_Socket; PinSocket_1x4
J3: Conn_01x08_Socket; PinSocket_1x8
J4: Conn_01x05_Socket; PinSocket_1x5
R1: 10, 1%; RESC0603
R2: 1G, 5%, 0603; RESC0603
U1: AD8615

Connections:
/2.5V: C1.1, J2.1, U1.5 (V+)
/-1.5V: C2.1, J2.3, U1.2 (V-)
/AD8615_Output: J4.2, U1.1
/BiasVoltage: J3.5, J3.6, J3.7, J3.8, J4.5
/Current: J3.1, J3.2, J3.3, J3.4, R2.1, U1.4 (-)
/ISO_GND: J1.2, J4.1, J4.4, U1.3 (+)
/PreVoltage: J4.3, R2.2
GND: C1.2, C2.2, J1.1, J2.2, J2.4, R1.2
unnamed: J1.3, R1.1

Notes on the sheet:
Excluded from BOM because already have 3 spares in stock from Phase 0.1

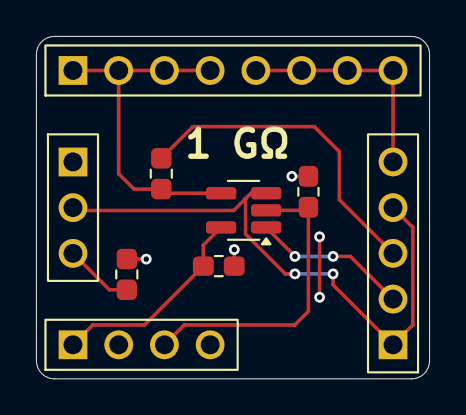
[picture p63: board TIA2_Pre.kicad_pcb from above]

Board: 2 copper layers, 21.8 x 19.0 mm, 9 parts (0 on the bottom side), 9 nets.

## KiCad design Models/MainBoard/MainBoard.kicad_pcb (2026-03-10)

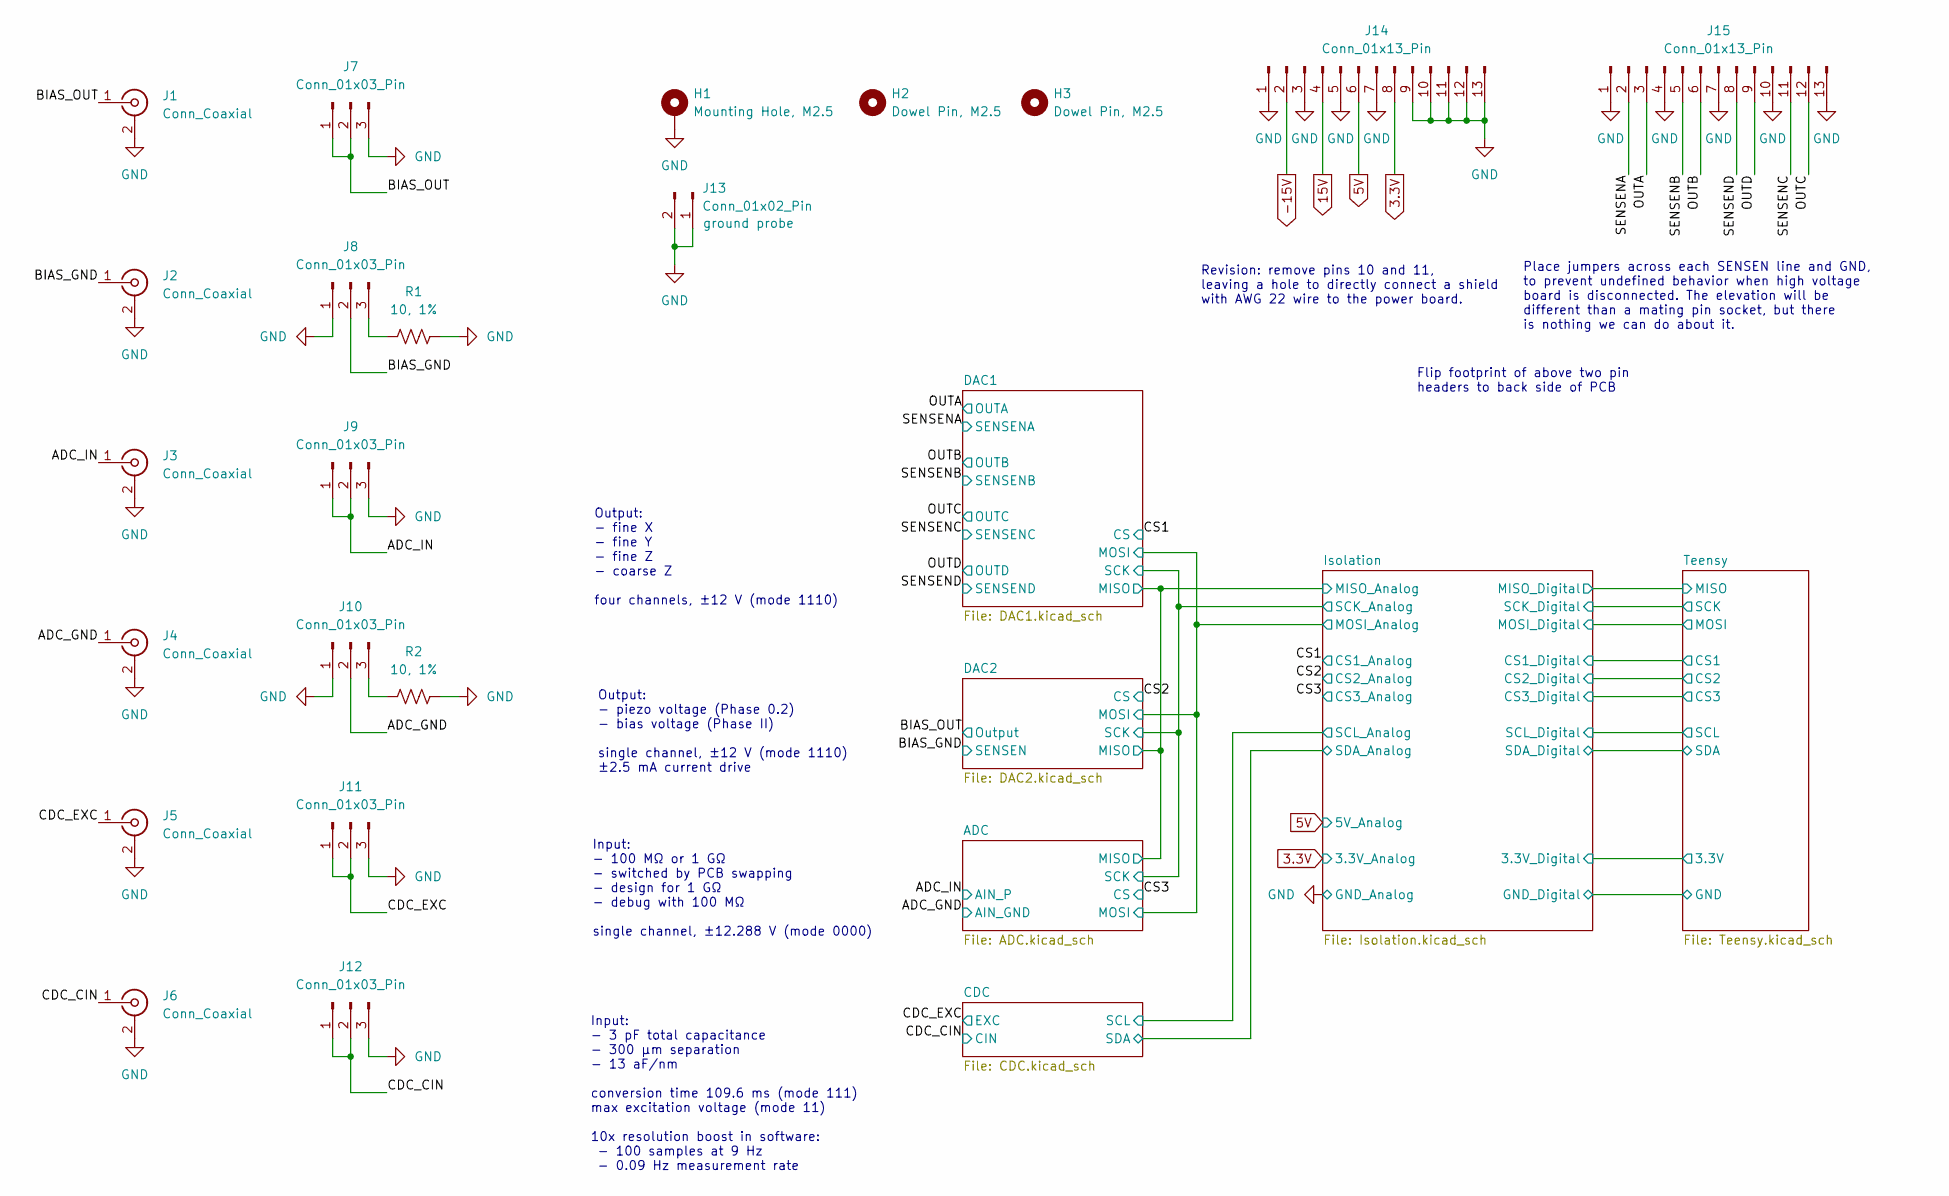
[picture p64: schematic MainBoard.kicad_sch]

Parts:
H1: Mounting Hole, M2.5; Keystone_24929
H2, H3: Dowel Pin, M2.5; DowelPin_2.5mm
J1, J2, J3, J4, J5, J6: Conn_Coaxial; Molex_MCX
J7, J8, J9, J10, J11, J12: Conn_01x03_Pin; PinHeader_1x3
J13: Conn_01x02_Pin; PinHeader_1x2
J14, J15: Conn_01x13_Pin; PinHeader_1x13
R1, R2: 10, 1%; RESC0603

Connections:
3.3V: J14.8; also elsewhere on the board
5V: J14.6; also elsewhere on the board
15V: J14.4; also elsewhere on the board
-15V: J14.2; also elsewhere on the board
/ADC_GND: J4.1 (In), J10.2; also elsewhere on the board
/ADC_IN: J3.1 (In), J9.1, J9.2; also elsewhere on the board
/BIAS_GND: J2.1 (In), J8.2; also elsewhere on the board
/BIAS_OUT: J1.1 (In), J7.1, J7.2; also elsewhere on the board
/CDC_CIN: J6.1 (In), J12.1, J12.2; also elsewhere on the board
/CDC_EXC: J5.1 (In), J11.1, J11.2; also elsewhere on the board
/OUTA: J15.3; also elsewhere on the board
/OUTB: J15.6; also elsewhere on the board
/OUTC: J15.12; also elsewhere on the board
/OUTD: J15.9; also elsewhere on the board
/SENSENA: J15.2; also elsewhere on the board
/SENSENB: J15.5; also elsewhere on the board
/SENSENC: J15.11; also elsewhere on the board
/SENSEND: J15.8; also elsewhere on the board
GND: H1.1, J1.2 (Ext), J2.2 (Ext), J3.2 (Ext), J4.2 (Ext), J5.2 (Ext), J6.2 (Ext), J7.3, J8.1, J9.3, J10.1, J11.3, J12.3, J13.1, J13.2, J14.1, J14.3, J14.5, J14.7, J14.9, J14.10, J14.11, J14.12, J14.13, J15.1, J15.4, J15.7, J15.10, J15.13, R1.2, R2.2; also elsewhere on the board
unnamed: J8.3, R1.1
unnamed: J10.3, R2.1

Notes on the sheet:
Output: - piezo voltage (Phase 0.2) - bias voltage (Phase II) single channel, ±12 V (mode 1110) ±2.5 mA current drive
Revision: remove pins 10 and 11, leaving a hole to directly connect a shield with AWG 22 wire to the power board.
Output: - fine X - fine Y - fine Z - coarse Z four channels, ±12 V (mode 1110)
Flip footprint of above two pin headers to back side of PCB
Input: - 100 MΩ or 1 GΩ - switched by PCB swapping - design for 1 GΩ - debug with 100 MΩ single channel, ±12.288 V (mode 0000)
Place jumpers across each SENSEN line and GND, to prevent undefined behavior when high voltage board is disconnected. The elevation will be different than a mating pin socket, but there is nothing we can do about it.
Input: - 3 pF total capacitance - 300 μm separation - 13 aF/nm conversion time 109.6 ms (mode 111) max excitation voltage (mode 11) 10x resolution boost in software: - 100 samples at 9 Hz - 0.09 Hz measurement rate

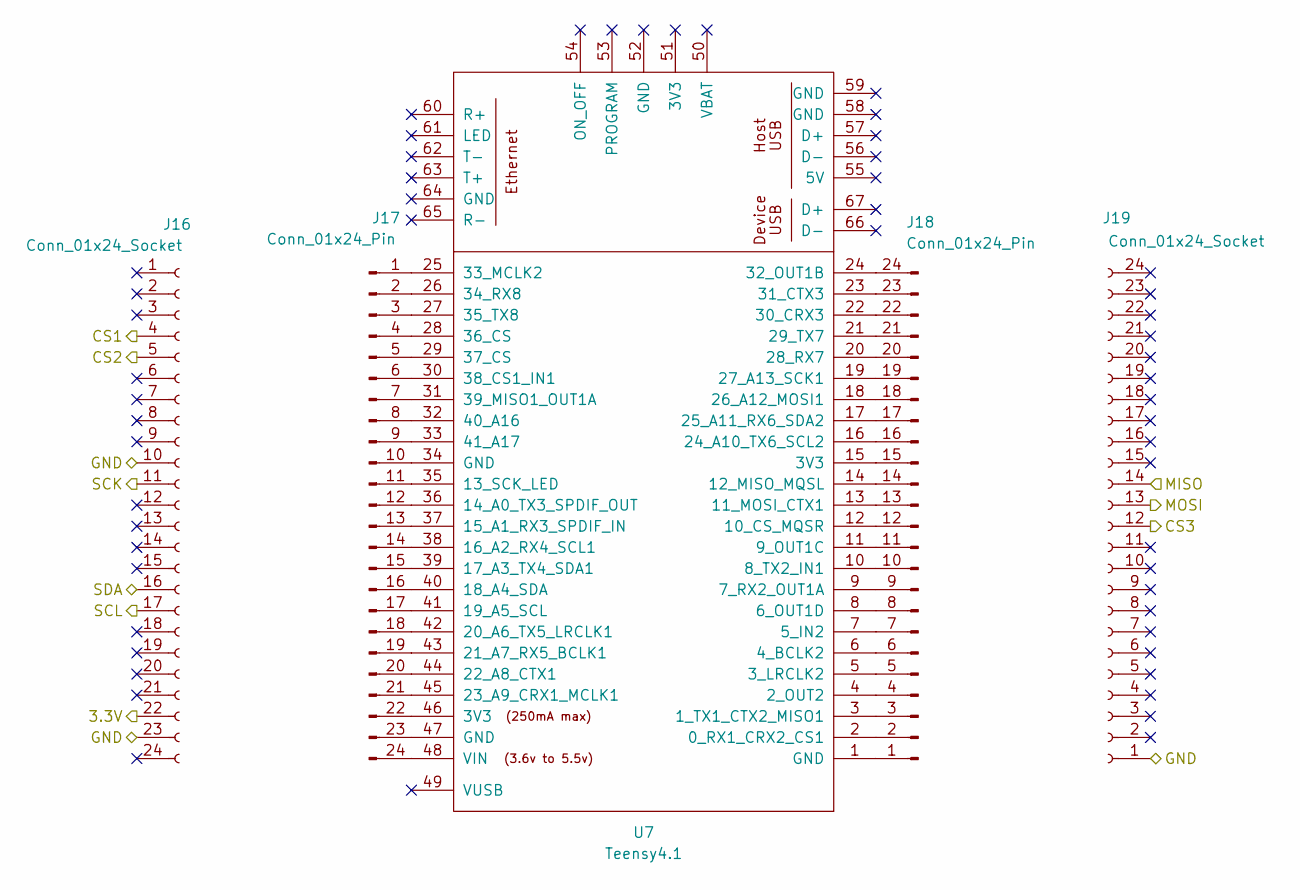
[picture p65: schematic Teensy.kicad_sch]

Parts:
J16, J19: Conn_01x24_Socket; PinSocket_1x24
J17, J18: Conn_01x24_Pin
U7: Teensy4.1

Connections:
/Isolation/3.3V_Digital: J16.22; also elsewhere on the board
/Isolation/CS1_Digital: J16.4; also elsewhere on the board
/Isolation/CS2_Digital: J16.5; also elsewhere on the board
/Isolation/CS3_Digital: J19.12; also elsewhere on the board
/Isolation/GND_Digital: J16.10, J16.23, J19.1; also elsewhere on the board
/Isolation/MISO_Digital: J19.14; also elsewhere on the board
/Isolation/MOSI_Digital: J19.13; also elsewhere on the board
/Isolation/SCK_Digital: J16.11; also elsewhere on the board
/Isolation/SCL_Digital: J16.17; also elsewhere on the board
/Isolation/SDA_Digital: J16.16; also elsewhere on the board
unnamed: J17.1, U7.25 (33_MCLK2)
unnamed: J17.2, U7.26 (34_RX8)
unnamed: J17.3, U7.27 (35_TX8)
unnamed: J17.4, U7.28 (36_CS)
unnamed: J17.5, U7.29 (37_CS)
unnamed: J17.6, U7.30 (38_CS1_IN1)
unnamed: J17.7, U7.31 (39_MISO1_OUT1A)
unnamed: J17.8, U7.32 (40_A16)
unnamed: J17.9, U7.33 (41_A17)
unnamed: J17.10, U7.34 (GND)
unnamed: J17.11, U7.35 (13_SCK_LED)
unnamed: J17.12, U7.36 (14_A0_TX3_SPDIF_OUT)
unnamed: J17.13, U7.37 (15_A1_RX3_SPDIF_IN)
unnamed: J17.14, U7.38 (16_A2_RX4_SCL1)
unnamed: J17.15, U7.39 (17_A3_TX4_SDA1)
unnamed: J17.16, U7.40 (18_A4_SDA)
unnamed: J17.17, U7.41 (19_A5_SCL)
unnamed: J17.18, U7.42 (20_A6_TX5_LRCLK1)
unnamed: J17.19, U7.43 (21_A7_RX5_BCLK1)
unnamed: J17.20, U7.44 (22_A8_CTX1)
unnamed: J17.21, U7.45 (23_A9_CRX1_MCLK1)
unnamed: J17.22, U7.46 (3V3)
unnamed: J17.23, U7.47 (GND)
unnamed: J17.24, U7.48 (VIN)
unnamed: J18.1, U7.1 (GND)
unnamed: J18.2, U7.2 (0_RX1_CRX2_CS1)
unnamed: J18.3, U7.3 (1_TX1_CTX2_MISO1)
unnamed: J18.4, U7.4 (2_OUT2)
unnamed: J18.5, U7.5 (3_LRCLK2)
unnamed: J18.6, U7.6 (4_BCLK2)
unnamed: J18.7, U7.7 (5_IN2)
unnamed: J18.8, U7.8 (6_OUT1D)
unnamed: J18.9, U7.9 (7_RX2_OUT1A)
unnamed: J18.10, U7.10 (8_TX2_IN1)
unnamed: J18.11, U7.11 (9_OUT1C)
unnamed: J18.12, U7.12 (10_CS_MQSR)
unnamed: J18.13, U7.13 (11_MOSI_CTX1)
unnamed: J18.14, U7.14 (12_MISO_MQSL)
unnamed: J18.15, U7.15 (3V3)
unnamed: J18.16, U7.16 (24_A10_TX6_SCL2)
unnamed: J18.17, U7.17 (25_A11_RX6_SDA2)
unnamed: J18.18, U7.18 (26_A12_MOSI1)
unnamed: J18.19, U7.19 (27_A13_SCK1)
unnamed: J18.20, U7.20 (28_RX7)
unnamed: J18.21, U7.21 (29_TX7)
unnamed: J18.22, U7.22 (30_CRX3)
unnamed: J18.23, U7.23 (31_CTX3)
unnamed: J18.24, U7.24 (32_OUT1B)

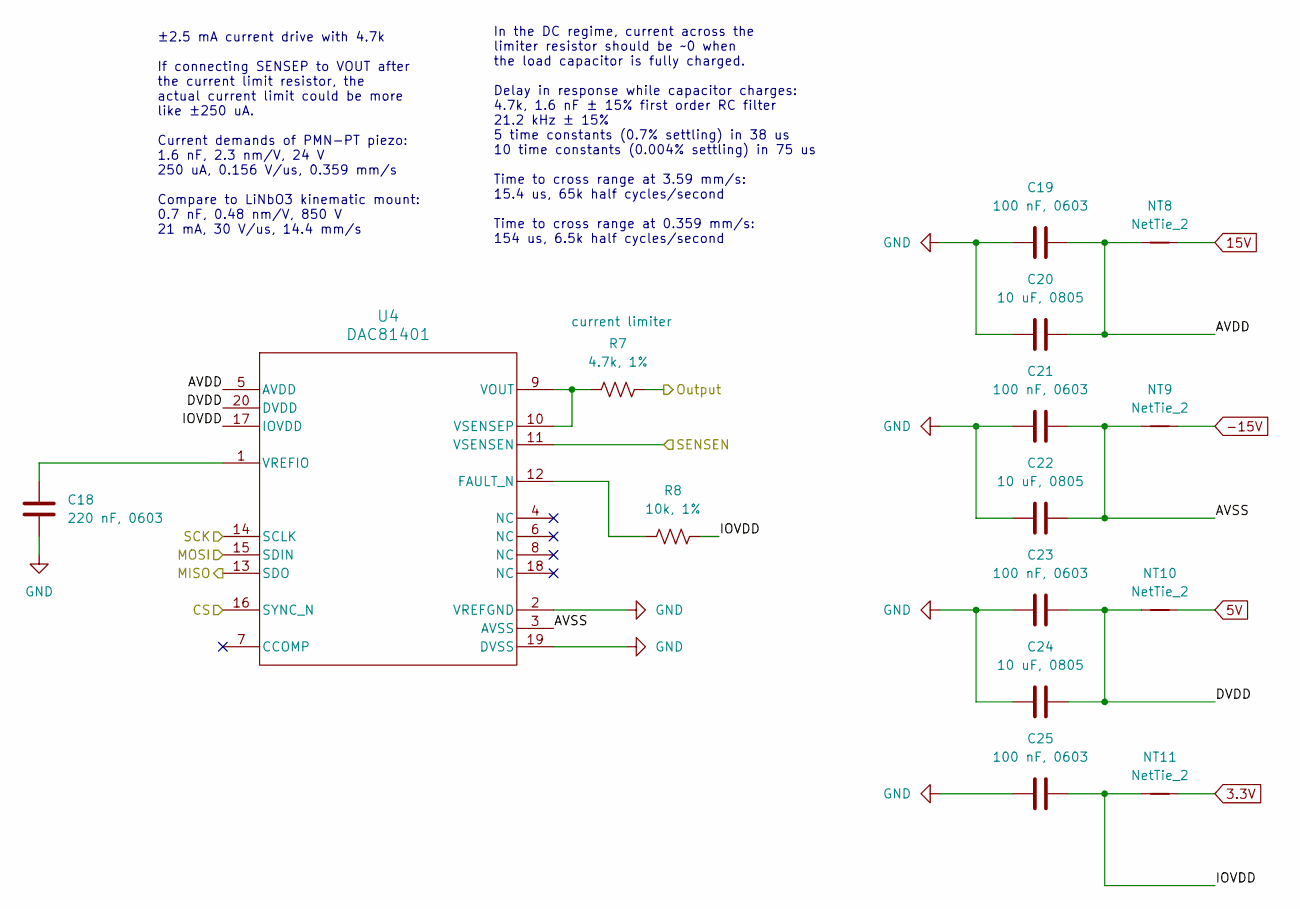
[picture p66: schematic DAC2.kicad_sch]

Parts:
C18: 220 nF, 0603; CAPC0603
C19, C21, C23, C25: 100 nF, 0603; CAPC0603
C20, C22, C24: 10 uF, 0805; CAPC0805
NT8, NT9, NT10, NT11: NetTie_2; NetTie_0.15mm
R7: 4.7k, 1%; RESC0603
R8: 10k, 1%; RESC0603
U4: DAC81401; TSSOP-20

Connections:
3.3V: NT11.2; also elsewhere on the board
5V: NT10.2; also elsewhere on the board
15V: NT8.2; also elsewhere on the board
-15V: NT9.2; also elsewhere on the board
/ADC/MISO: U4.13 (SDO); also elsewhere on the board
/ADC/MOSI: U4.15 (SDIN); also elsewhere on the board
/ADC/SCK: U4.14 (SCLK); also elsewhere on the board
/BIAS_GND: U4.11 (VSENSEN); also elsewhere on the board
/BIAS_OUT: R7.2; also elsewhere on the board
/CS2: U4.16 (SYNC_N); also elsewhere on the board
/DAC2/AVDD: C19.2, C20.2, NT8.1, U4.5 (AVDD)
/DAC2/AVSS: C21.2, C22.2, NT9.1, U4.3 (AVSS)
/DAC2/DVDD: C23.2, C24.2, NT10.1, U4.20 (DVDD)
/DAC2/IOVDD: C25.2, NT11.1, R8.2, U4.17 (IOVDD)
GND: C18.2, C19.1, C20.1, C21.1, C22.1, C23.1, C24.1, C25.1, U4.2 (VREFGND), U4.19 (DVSS); also elsewhere on the board
unnamed: R8.1, U4.12 (FAULT_N)
unnamed: R7.1, U4.9 (VOUT), U4.10 (VSENSEP)
unnamed: C18.1, U4.1 (VREFIO)

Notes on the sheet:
±2.5 mA current drive with 4.7k If connecting SENSEP to VOUT after the current limit resistor, the actual current limit could be more like ±250 uA. Current demands of PMN-PT piezo: 1.6 nF, 2.3 nm/V, 24 V 250 uA, 0.156 V/us, 0.359 mm/s Compare to LiNbO3 kinematic mount: 0.7 nF, 0.48 nm/V, 850 V 21 m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
In the DC regime, current across the limiter resistor should be ~0 when the load capacitor is fully charged. Delay in response while capacitor charges: 4.7k, 1.6 nF ± 15% first order RC filter 21.2 kHz ± 15% 5 time constants (0.7% settling) in 38 us 10 time constants (0.004% settling) in 75 us Time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

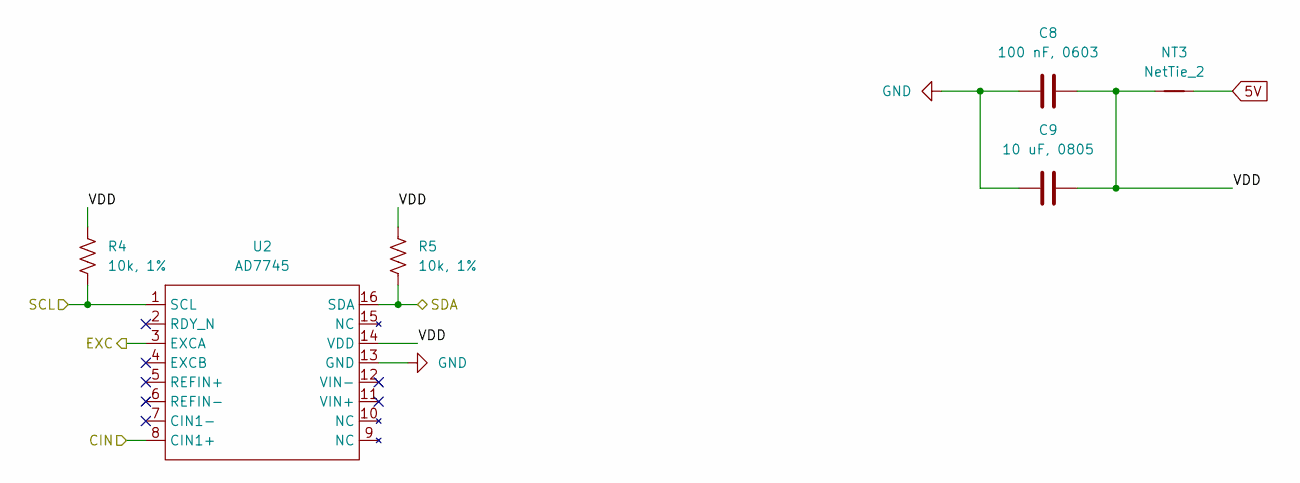
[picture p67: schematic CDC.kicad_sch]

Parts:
C8: 100 nF, 0603; CAPC0603
C9: 10 uF, 0805; CAPC0805
NT3: NetTie_2; NetTie_0.15mm
R4, R5: 10k, 1%; RESC0603
U2: AD7745; TSSOP-16

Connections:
5V: NT3.2; also elsewhere on the board
/CDC/SCL: R4.2, U2.1 (SCL); also elsewhere on the board
/CDC/SDA: R5.2, U2.16 (SDA); also elsewhere on the board
/CDC/VDD: C8.2, C9.2, NT3.1, R4.1, R5.1, U2.14 (VDD)
/CDC_CIN: U2.8 (CIN1+); also elsewhere on the board
/CDC_EXC: U2.3 (EXCA); also elsewhere on the board
GND: C8.1, C9.1, U2.13 (GND); also elsewhere on the board

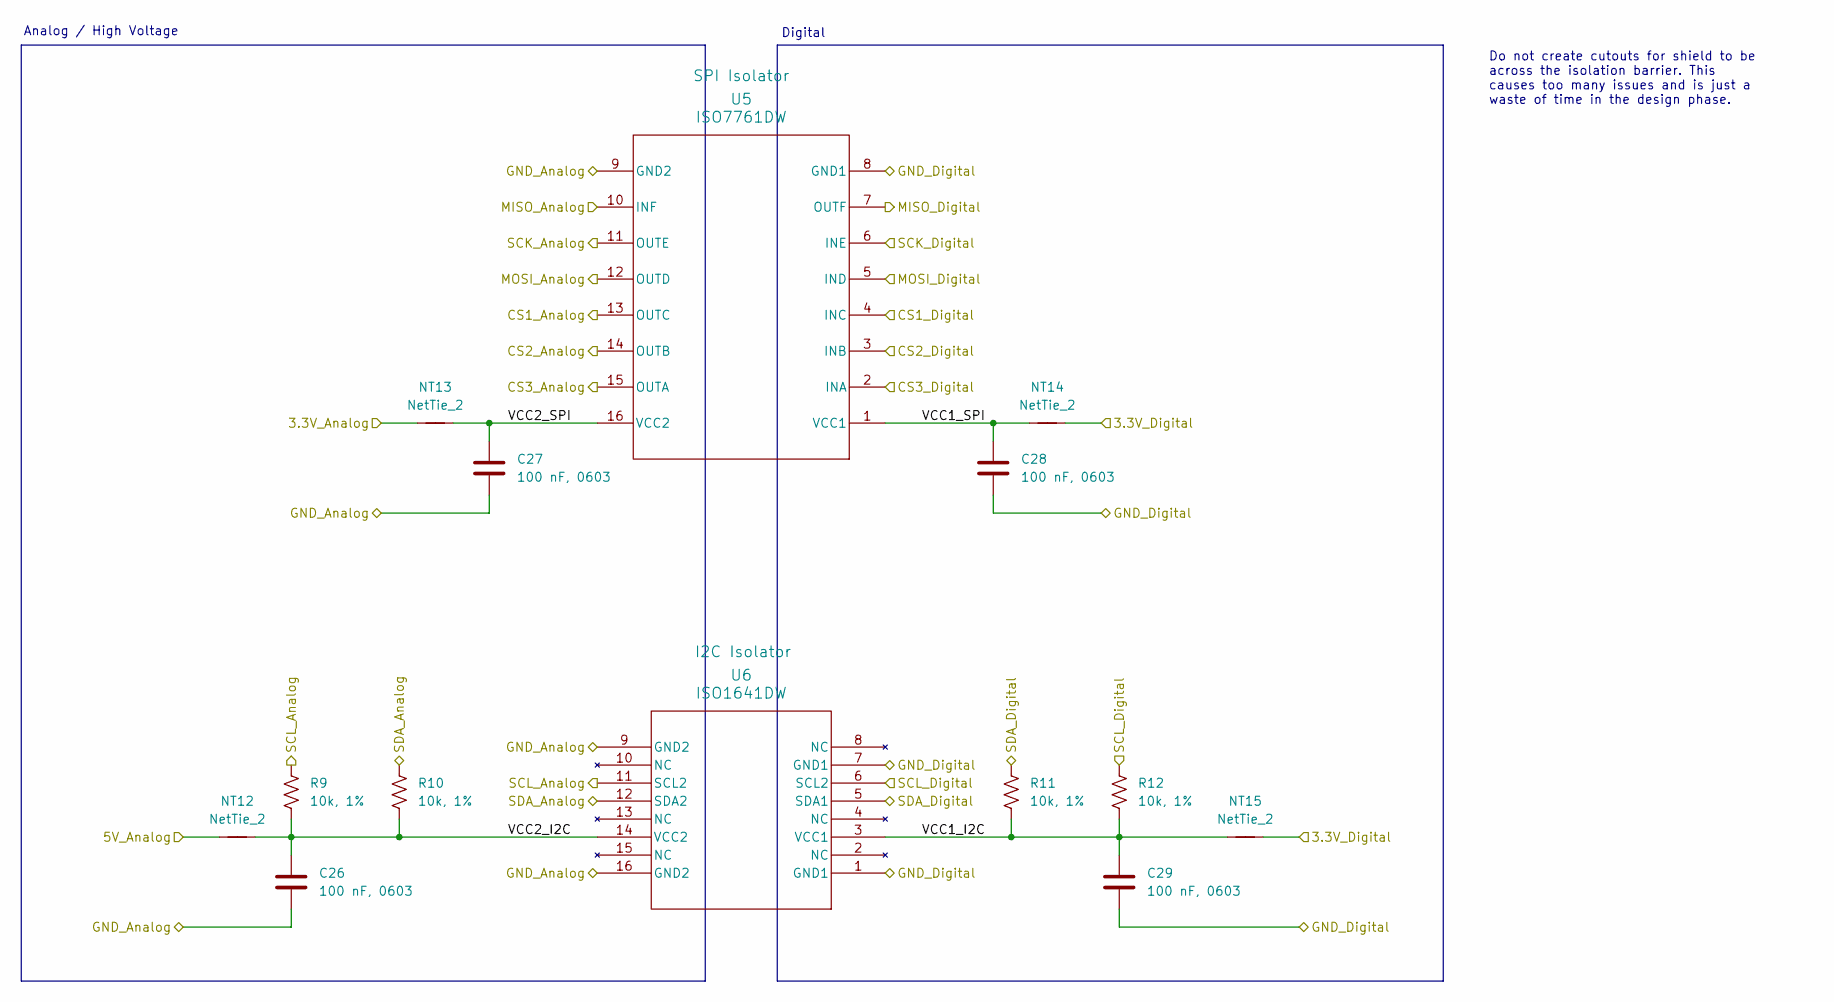
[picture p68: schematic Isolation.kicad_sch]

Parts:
C26, C27, C28, C29: 100 nF, 0603; CAPC0603
NT12, NT13, NT14, NT15: NetTie_2; NetTie_0.15mm
R9, R10, R11, R12: 10k, 1%; RESC0603
U5: ISO7761DW; SOIC-16-Wide
U6: ISO1641DW; SOIC-16-Wide

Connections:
3.3V: NT13.1; also elsewhere on the board
5V: NT12.1; also elsewhere on the board
/ADC/MISO: U5.10 (INF); also elsewhere on the board
/ADC/MOSI: U5.12 (OUTD); also elsewhere on the board
/ADC/SCK: U5.11 (OUTE); also elsewhere on the board
/CDC/SCL: R9.1, U6.11 (SCL2); also elsewhere on the board
/CDC/SDA: R10.1, U6.12 (SDA2); also elsewhere on the board
/CS1: U5.13 (OUTC); also elsewhere on the board
/CS2: U5.14 (OUTB); also elsewhere on the board
/CS3: U5.15 (OUTA); also elsewhere on the board
/Isolation/3.3V_Digital: NT14.2, NT15.2; also elsewhere on the board
/Isolation/CS1_Digital: U5.4 (INC); also elsewhere on the board
/Isolation/CS2_Digital: U5.3 (INB); also elsewhere on the board
/Isolation/CS3_Digital: U5.2 (INA); also elsewhere on the board
/Isolation/GND_Digital: C28.2, C29.2, U5.8 (GND1), U6.1 (GND1), U6.7 (GND1); also elsewhere on the board
/Isolation/MISO_Digital: U5.7 (OUTF); also elsewhere on the board
/Isolation/MOSI_Digital: U5.5 (IND); also elsewhere on the board
/Isolation/SCK_Digital: U5.6 (INE); also elsewhere on the board
/Isolation/SCL_Digital: R12.1, U6.6 (SCL2); also elsewhere on the board
/Isolation/SDA_Digital: R11.1, U6.5 (SDA1); also elsewhere on the board
/Isolation/VCC1_I2C: C29.1, NT15.1, R11.2, R12.2, U6.3 (VCC1)
/Isolation/VCC1_SPI: C28.1, NT14.1, U5.1 (VCC1)
/Isolation/VCC2_I2C: C26.1, NT12.2, R9.2, R10.2, U6.14 (VCC2)
/Isolation/VCC2_SPI: C27.1, NT13.2, U5.16 (VCC2)
GND: C26.2, C27.2, U5.9 (GND2), U6.9 (GND2), U6.16 (GND2); also elsewhere on the board

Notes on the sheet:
Do not create cutouts for shield to be across the isolation barrier. This causes too many issues and is just a waste of time in the design phase.
Analog / High Voltage
Digital

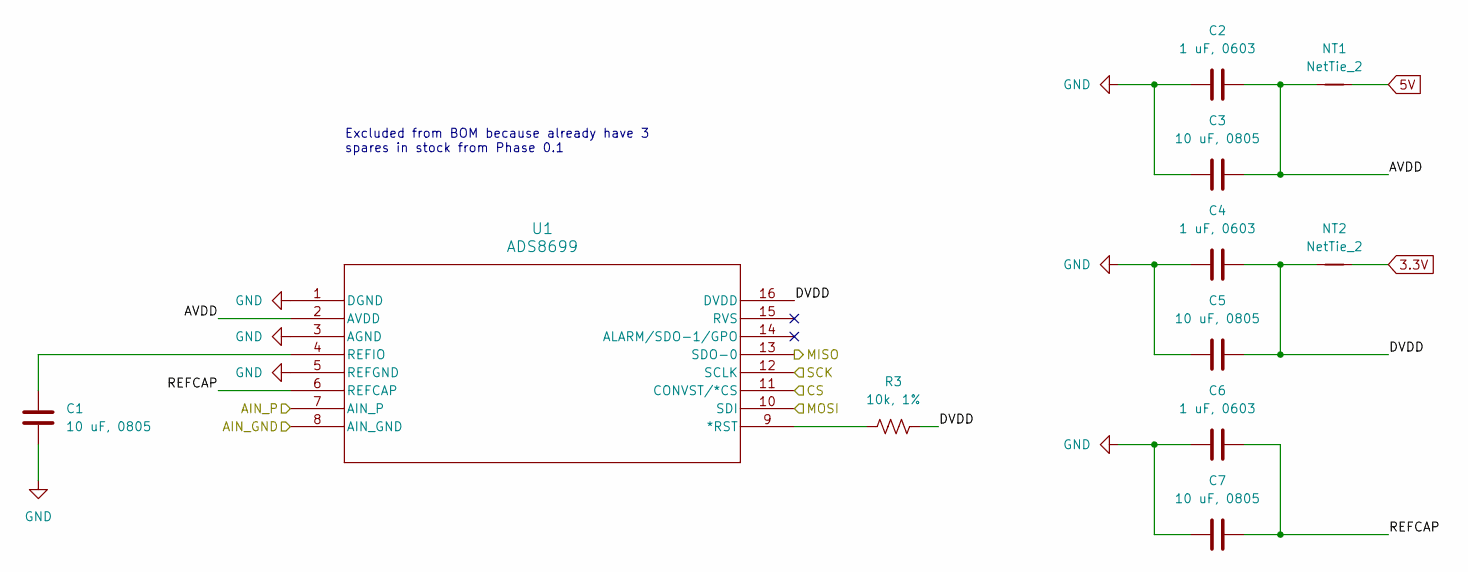
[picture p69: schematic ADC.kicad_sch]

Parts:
C1, C3, C5, C7: 10 uF, 0805; CAPC0805
C2, C4, C6: 1 uF, 0603; CAPC0603
NT1, NT2: NetTie_2; NetTie_0.15mm
R3: 10k, 1%; RESC0603
U1: ADS8699; TSSOP-16

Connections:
3.3V: NT2.2; also elsewhere on the board
5V: NT1.2; also elsewhere on the board
/ADC/AVDD: C2.2, C3.2, NT1.1, U1.2 (AVDD)
/ADC/DVDD: C4.2, C5.2, NT2.1, R3.2, U1.16 (DVDD)
/ADC/MISO: U1.13 (SDO-0); also elsewhere on the board
/ADC/MOSI: U1.10 (SDI); also elsewhere on the board
/ADC/REFCAP: C6.2, C7.2, U1.6 (REFCAP)
/ADC/SCK: U1.12 (SCLK); also elsewhere on the board
/ADC_GND: U1.8 (AIN_GND); also elsewhere on the board
/ADC_IN: U1.7 (AIN_P); also elsewhere on the board
/CS3: U1.11 (CONVST/*CS); also elsewhere on the board
GND: C1.2, C2.1, C3.1, C4.1, C5.1, C6.1, C7.1, U1.1 (DGND), U1.3 (AGND), U1.5 (REFGND); also elsewhere on the board
unnamed: R3.1, U1.9 (*RST)
unnamed: C1.1, U1.4 (REFIO)

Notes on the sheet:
Excluded from BOM because already have 3 spares in stock from Phase 0.1

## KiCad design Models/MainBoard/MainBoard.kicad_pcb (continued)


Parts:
C10: 220 nF, 0603; CAPC0603
C11, C13, C15, C17: 100 nF, 0603; CAPC0603
C12, C14, C16: 10 uF, 0805; CAPC0805
NT4, NT5, NT6, NT7: NetTie_2; NetTie_0.15mm
R6: 10k, 1%; RESC0603
U3: DAC81404; VQFN-32

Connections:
3.3V: NT7.2; also elsewhere on the board
5V: NT6.2; also elsewhere on the board
15V: NT4.2; also elsewhere on the board
-15V: NT5.2; also elsewhere on the board
/ADC/MISO: U3.9 (SDO); also elsewhere on the board
/ADC/MOSI: U3.11 (SDIN); also elsewhere on the board
/ADC/SCK: U3.10 (SCLK); also elsewhere on the board
/CS1: U3.12 (SYNC_N); also elsewhere on the board
/DAC1/AVDD: C11.2, C12.2, NT4.1, U3.28 (AVDD)
/DAC1/AVSS: C13.2, C14.2, NT5.1, U3.27 (AVSS)
/DAC1/DVDD: C15.2, C16.2, NT6.1, U3.30 (DVDD)
/DAC1/IOVDD: C17.2, NT7.1, R6.1, U3.13 (LDAC_N), U3.15 (IOVDD), U3.16 (CLR_N), U3.32 (RST_N)
/OUTA: U3.1 (OUTA), U3.3 (SENSEPA); also elsewhere on the board
/OUTB: U3.6 (SENSEPB), U3.8 (OUTB); also elsewhere on the board
/OUTC: U3.17 (OUTC), U3.19 (SENSEPC); also elsewhere on the board
/OUTD: U3.22 (SENSEPD), U3.24 (OUTD); also elsewhere on the board
/SENSENA: U3.4 (SENSENA); also elsewhere on the board
/SENSENB: U3.5 (SENSENB); also elsewhere on the board
/SENSENC: U3.20 (SENSENC); also elsewhere on the board
/SENSEND: U3.21 (SENSEND); also elsewhere on the board
GND: C10.2, C11.1, C12.1, C13.1, C14.1, C15.1, C16.1, C17.1, U3.14 (GND), U3.25 (REFGND), U3.29 (AGND), U3.33 (Thermal_pad); also elsewhere on the board
unnamed: R6.2, U3.31 (FAULT_N)
unnamed: C10.1, U3.26 (REFIO)

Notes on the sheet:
Orient at right angle so digital pins come out from the bottom
For the piezo driver channels, the load (28k resistor) sits on a different board. We want the GND side of that resistor to sit at the same potential as the non-inverting input to the PA95 op amp. SENSEN detects the IR drop from difference in ground potentials (large power currents). Such currents d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



Board: 4 copper layers, 77.0 x 62.5 mm, 82 parts (13 on the bottom side), 62 nets.

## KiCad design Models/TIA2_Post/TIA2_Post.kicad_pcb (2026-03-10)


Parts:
H1, H2: MountingHole; DowelPin_2.5mm
J1: Conn_01x03_Pin; PinHeader_1x3
J2: Conn_01x03_Socket; PinSocket_1x3
J3: Conn_01x06_Socket; PinSocket_1x6
R1: 10, 1%; RESC0603

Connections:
15V: J3.1; also elsewhere on the board
-15V: J3.3; also elsewhere on the board
/AD8615_Output: J2.2; also elsewhere on the board
/PostVoltage: J3.5; also elsewhere on the board
/PreVoltage: J2.3; also elsewhere on the board
GND: J1.1, J3.2, J3.4, R1.2; also elsewhere on the board
ISO_GND: J1.2, J2.1, J3.6; also elsewhere on the board
unnamed: J1.3, R1.1


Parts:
D1, D2, D3, D4: 1N4448W; SOD-123
D5, D6: 10V, 1%; SOT-23
J4, J5: Conn_01x02_Pin; PinHeader_1x2
Q1: Q_PNP_BEC; SOT-23
Q2: Q_NPN_BEC; SOT-23
R5: 240k, 1%; RESC0603
R6, R9, R10: 10k, 1%; RESC0603
R7, R8: 1k, 1%; RESC0603

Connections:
15V: R9.1; also elsewhere on the board
-15V: R10.2; also elsewhere on the board
/Amplifier/InvertingInput: J4.2; also elsewhere on the board
/Limiter/Clamped_Output: J5.1, Q1.3 (C), Q2.3 (C)
/PostVoltage: R5.1, R7.1, R8.1; also elsewhere on the board
GND: D5.2 (A), D5.3 (*), D6.1 (K); also elsewhere on the board
ISO_GND: R6.2; also elsewhere on the board
unnamed: D1.2 (A), D2.1 (K), J4.1
unnamed: D1.1 (K), D2.2 (A), J5.2, R5.2, R6.1
unnamed: D3.2 (A), R7.2
unnamed: D3.1 (K), Q1.2 (E)
unnamed: D4.2 (A), Q2.2 (E)
unnamed: D4.1 (K), R8.2
unnamed: D5.1 (K), Q1.1 (B), R9.2
unnamed: D6.2 (A), D6.3 (*), Q2.1 (B), R10.1

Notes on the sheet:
Transistors, Zeners, 1k, 1N4448W: Use stock from Phase 0.1


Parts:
C1, C2: 100 nF, 0603; CAPC0603
R2: 1k, 1%; RESC0603
R3: 24k, 1%; RESC0603
U1: OP37G; SOIC-8

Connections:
15V: C1.1, U1.7 (V+); also elsewhere on the board
-15V: C2.1, U1.4 (V-); also elsewhere on the board
/AD8615_Output: U1.3 (+); also elsewhere on the board
/Amplifier/InvertingInput: R2.2, R3.1, U1.2 (-); also elsewhere on the board
/PostVoltage: R3.2, U1.6; also elsewhere on the board
GND: C1.2, C2.2; also elsewhere on the board
ISO_GND: R2.1; also elsewhere on the board


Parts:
C3: 2 nF, 1%; CAPC0603
R4: 1.3k, 1%; RESC0603
RV1: 10k, 10%; Bourns_3296Y
RV2: 200k, 10%; Bourns_3296Y

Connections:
/PostVoltage: RV2.1, RV2.2; also elsewhere on the board
/PreVoltage: C3.1, RV2.3; also elsewhere on the board
ISO_GND: RV1.1, RV1.2; also elsewhere on the board
unnamed: C3.2, R4.1
unnamed: R4.2, RV1.3

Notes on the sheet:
2 nF, 1.3k, Trimpots: Use stock from Phase 0.1


Board: 2 copper layers, 39.3 x 26.9 mm, 31 parts (0 on the bottom side), 20 nets.

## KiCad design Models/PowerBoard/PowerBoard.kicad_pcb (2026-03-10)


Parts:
H1, H2, H4: Mounting Hole, M2.5; Keystone_24929
H3, H5: Dowel Pin, M2.5; DowelPin_2.5mm
J1, J2, J3, J4: Conn_Coaxial; Molex_MCX
J5, J6, J7, J8, J9, J10: Conn_01x03_Pin; PinHeader_1x3
J11: Conn_01x13_Socket; PinSocket_1x13

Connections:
5V_PreAmp: J8.1, J8.2; also elsewhere on the board
-5V_PreAmp: J7.1, J7.2; also elsewhere on the board
/2.5V: J4.1 (In), J10.1, J10.2; also elsewhere on the board
/3.3V: J11.8; also elsewhere on the board
/5V: J11.6; also elsewhere on the board
/15V: J2.1 (In), J6.1, J6.2, J11.4; also elsewhere on the board
/-1.5V: J3.1 (In), J9.1, J9.2; also elsewhere on the board
/-15V: J1.1 (In), J5.1, J5.2, J11.2; also elsewhere on the board
GND: H1.1, H2.1, H4.1, J1.2 (Ext), J2.2 (Ext), J3.2 (Ext), J4.2 (Ext), J5.3, J6.3, J7.3, J8.3, J9.3, J10.3, J11.1, J11.3, J11.5, J11.7, J11.9, J11.10, J11.11, J11.12, J11.13; also elsewhere on the board

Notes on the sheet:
18V: no external interface -18V: no external interface
5V (preamp): breadboard -5V (preamp): breadboard 2.5V: shielded -1.5V: shielded
15V: shielded -15V: shielded
5V: no external interface 3.3V: no external interface


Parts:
C1: 220 nF, 0603; CAPC0603
C4, C5: 1 uF, 0603; CAPC0603
C7: 100 nF, 0603; CAPC0603
D1, D4: 1N4007W; SOD-123FL
D5, D7: D_Schottky; SOD-123
U1: LM7815, 15V, 5%; TO-220
U3: LM7915, -15V, 5%; TO-220

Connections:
/15V: C7.1, D1.2 (A), D7.1 (K), U1.3 (OUT); also elsewhere on the board
/15V/18V: C1.1, D1.1 (K), U1.1 (IN); also elsewhere on the board
/15V/-18V: C5.1, D4.2 (A), U3.2 (IN); also elsewhere on the board
/-15V: C4.2, D4.1 (K), D5.2 (A), U3.3 (OUT); also elsewhere on the board
GND: C1.2, C4.1, C5.2, C7.2, D5.1 (K), D7.2 (A), U1.2 (GND), U3.1 (GND); also elsewhere on the board

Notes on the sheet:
Hand-solder a 10 uF, 0805 capacitor on top of the 1 uF output capacitor to minimize instabilities that cause 70-125 kHz oscillations in TIA1 and TIA2.


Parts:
BT1: TP-3005D-3
J12: Banana Socket, Red; Multicomp_24.243
J13: Banana Socket, Black; Multicomp_24.243
J14: Banana Socket, Yellow; Multicomp_24.243

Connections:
/15V/18V: J12.1, J12.2; also elsewhere on the board
/15V/-18V: J14.1, J14.2; also elsewhere on the board
GND: J13.1, J13.2; also elsewhere on the board


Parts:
C9: 220 nF, 0603; CAPC0603
C10, C11: 1 uF, 0603; CAPC0603
C12: 100 nF, 0603; CAPC0603
C13, C14: 10 uF, 0805; CAPC0805
D9, D10: 1N4007W; SOD-123FL
D11, D12: D_Schottky; SOD-123
RV1, RV2: 1k, 10%; Bourns_3296Y
U5: LM7805, 5V, 5%; TO-220
U6: LM7905, -5V, 5%; TO-220

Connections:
5V_PreAmp: C12.1, D9.2 (A), D12.1 (K), RV1.3, U5.3 (OUT); also elsewhere on the board
-5V_PreAmp: C10.2, D10.1 (K), D11.2 (A), RV2.3, U6.3 (OUT); also elsewhere on the board
/2.5V: C13.1, RV1.2; also elsewhere on the board
/15V/18V: C9.1, D9.1 (K), U5.1 (IN); also elsewhere on the board
/15V/-18V: C11.1, D10.2 (A), U6.2 (IN); also elsewhere on the board
/-1.5V: C14.2, RV2.2; also elsewhere on the board
GND: C9.2, C10.1, C11.2, C12.2, C13.2, C14.1, D11.1 (K), D12.2 (A), RV1.1, RV2.1, U5.2 (GND), U6.1 (GND); also elsewhere on the board


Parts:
C2: 220 nF, 0603; CAPC0603
C3, C6: 1 uF, 0603; CAPC0603
C8: 100 nF, 0603; CAPC0603
D2: 1N4007W; SOD-123FL
D3, D6, D8: D_Schottky; SOD-123
U2: LM7805, 5V, 5%; TO-220
U4: TLV76133, 3.3V, 1%; SOT-223

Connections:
/3.3V: C6.1, D3.2 (A), D6.1 (K), U4.4 (OUT); also elsewhere on the board
/5V: C3.1, C8.1, D2.2 (A), D3.1 (K), D8.1 (K), U2.3 (OUT), U4.3 (IN); also elsewhere on the board
/15V/18V: C2.1, D2.1 (K), U2.1 (IN); also elsewhere on the board
GND: C2.2, C3.2, C6.2, C8.2, D6.2 (A), D8.2 (A), U2.2 (GND), U4.1 (GND); also elsewhere on the board

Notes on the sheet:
C3 and C8 incorrectly had their positions swapped during PCB layout.


Board: 2 copper layers, 81.1 x 47.1 mm, 53 parts (0 on the bottom side), 11 nets.

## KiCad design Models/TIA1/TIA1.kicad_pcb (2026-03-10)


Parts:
C1, C2: 100 nF, 0603; CAPC0603
J1: Conn_01x03_Pin; PinHeader_1x3
J2, J3: Conn_01x08_Socket; PinSocket_1x8
R1: 100M, 5%, 0603; RESC0603
R2: 10, 1%; RESC0603
U1: OPA828; SOIC-8

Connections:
/15V: C1.1, J3.3, U1.7 (V+)
/-15V: C2.1, J3.1, U1.4 (V-)
/BiasVoltage: J2.5, J2.6, J2.7, J2.8, J3.7
/Current: J2.1, J2.2, J2.3, J2.4, R1.1, U1.2 (-)
/ISO_GND: J1.2, J3.6, J3.8, U1.3 (+)
/PostVoltage: J3.5, R1.2, U1.6
GND: C1.2, C2.2, J1.1, J3.2, J3.4, R2.2
unnamed: J1.3, R2.1


Board: 2 copper layers, 21.8 x 19.0 mm, 8 parts (0 on the bottom side), 8 nets.

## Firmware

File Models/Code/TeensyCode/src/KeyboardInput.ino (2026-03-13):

#include "KeyboardInput.h"

#include "ADC.h"
#include "RingBuffer.h"
#include "TimeStatistics.h"

void timeFidelityDiagnosticLoop() {
  delay(500);

  Serial.println();
  Serial.println(timeStatistics.above1000000us_jumps);
  Serial.println(timeStatistics.above100000us_jumps);
  Serial.println(timeStatistics.above10000us_jumps);
  Serial.println(timeStatistics.above1000us_jumps);
  Serial.println(timeStatistics.above100us_jumps);
  Serial.println(timeStatistics.above20us_jumps);
  Serial.println(timeStatistics.exactly20us_jumps);
  Serial.println(timeStatistics.under20us_jumps);
  Serial.println(timeStatistics.total_jumps);
}

void adcResponsivenessDiagnosticLoop() {
  if (Serial.available() > 0) {
    char incomingByte = Serial.read();

    if (incomingByte == 'c') {
      Serial.println("received command 'c'");

      float voltage = ADC::readConversionCode();
      Serial.print("ADC code (fraction of full-scale): ");
      Serial.println(voltage, 6); // force it to 6 decimal places
    } else if (incomingByte == 'd') {
      Serial.println("received command 'd'");
      
      uint32_t rangeCode = ADC::readRangeSelect();
      Serial.print("Contents of range select register: ");
      Serial.println(rangeCode);
    } else if (incomingByte == '0') {
      Serial.println("received command '0'");
      
      ADC::writeRangeSelect(0b0000);
    } else if (incomingByte == '1') {
      Serial.println("received command '1'");
      
      ADC::writeRangeSelect(0b0001);
    }
  }
}

char oscilloscopeMode = '0';
float oscilloscopeCopiedSamples[1000];
uint32_t oscilloscopeAveragedGroupCount = 0;

void oscilloscopeGuardedCode(bool shouldDisplayLatest) {
  uint32_t previousSlotID = (oscilloscopeTimestamp - startTimestamp) / 20;
  uint32_t currentSlotID = (latestTimestamp - startTimestamp) / 20;

  if (shouldDisplayLatest) {
    // WARNING: Modulo operator may have undefined behavior for
    // negative integers. Force the number to be positive.
    int32_t endSlotID = currentSlotID + 1;
    int32_t startSlotID = endSlotID - 1000;
    endSlotID += 50000;
    startSlotID += 50000;
    if (startSlotID < 0) {
      Serial.println("Invalid slot ID.");
      exit(0);
    }

    for (int32_t slotID = startSlotID; slotID < endSlotID; ++slotID) {
      int32_t copiedSampleID = slotID - startSlotID;
      float sample = ringBuffer.samples[slotID % 50000];
      oscilloscopeCopiedSamples[copiedSampleID] = sample;
    }
  } else if (oscilloscopeMode == 'a') {
    // Average every group of 50 samples as it gets completed.
    // A group is in progress if modulo previousSlotID = 0...49.
    uint32_t previousInProgressID = previousSlotID / 50;
    uint32_t currentInProgressID = currentSlotID / 50;
    if (currentInProgressID - previousInProgressID > 900) {
      Serial.println("Buffer overflow, in-progress data may wrap around and overwrite finished groups.");
      exit(0);
    }
    if (currentInProgressID - previousInProgressID > 300) {
      Serial.println("Buffer overflow, exceeded buffer size allocated for copied samples.");
      exit(0);
    }

    for (
      uint32_t groupID = previousInProgressID;
      groupID < currentInProgressID;
      ++groupID
    ) {
      uint32_t copiedGroupID = groupID - previousInProgressID;

      float minimum = 1e38;
      float sum = 0;
      float maximum = -1e38;
      for (uint32_t indexInGroup = 0; indexInGroup < 50; ++indexInGroup) {
        uint32_t slotID = groupID * 50 + indexInGroup;
        float sample = ringBuffer.samples[slotID % 50000];

        minimum = min(minimum, sample);
        sum += sample;
        maximum = max(maximum, sample);
      }
      float average = sum / 50;

      oscilloscopeCopiedSamples[copiedGroupID * 3 + 0] = minimum;
      oscilloscopeCopiedSamples[copiedGroupID * 3 + 1] = average;
      oscilloscopeCopiedSamples[copiedGroupID * 3 + 2] = maximum;
    }

    oscilloscopeAveragedGroupCount =
    currentInProgressID - previousInProgressID;
  }

  oscilloscopeTimestamp = latestTimestamp;
}

bool getShouldCopyLatest() {
  if (oscilloscopeMode == 'l') {
    return true;
  } else if (oscilloscopeMode == 'z') {
    return true;
  } else {
    return false;
  }
}

uint32_t staticDisplayTimeNext = 0;
bool getShouldDisplayLatest() {
  if (!getShouldCopyLatest()) {
    return false;
  }
  
  if (oscilloscopeTimestamp < staticDisplayTimeNext) {
    return false;
  }

  staticDisplayTimeNext = max(oscilloscopeTimestamp, staticDisplayTimeNext + 1000000);

  return true;
}

void oscilloscopeDiagnosticLoop() {
  delay(20);

  if (Serial.available() > 0) {
    char incomingByte = Serial.read();

    if (incomingByte == 'a') {
      oscilloscopeMode = 'a';
    } else if (incomingByte == 'l') {
      oscilloscopeMode = 'l';
    } else if (incomingByte == 'z') {
      oscilloscopeMode = 'z';
    } else if (incomingByte == '0') {
      oscilloscopeMode = '0';
    }
  }
  
  // Make the guarded portion very small and do not
  // invoke 'Serial.print' here.
  oscilloscopeLock = true;
  oscilloscopeGuardedCode(getShouldCopyLatest());
  oscilloscopeLock = false;

  if (getShouldDisplayLatest()) {
    if (oscilloscopeMode == 'l') {
      for (uint32_t sampleID = 0; sampleID < 1000; ++sampleID) {
        float sample = oscilloscopeCopiedSamples[sampleID];
        Serial.print(">voltage:");
        Serial.print(sampleID);
        Serial.print(":");
        Serial.println(sample, 4);
      }
    } else if (oscilloscopeMode == 'z') {
      for (uint32_t sampleID = 0; sampleID < 100; ++sampleID) {
        float sample = oscilloscopeCopiedSamples[900 + sampleID];
        for (uint32_t i = 0; i < 10; ++i) {
          Serial.print(">voltage:");
          Serial.print(sampleID * 10 + i);
          Serial.print(":");
          Serial.println(sample, 4);
        }
      }
    }

    Serial.print("current timestamp: ");
    Serial.println(oscilloscopeTimestamp);
    Serial.print("next display timestamp: ");
    Serial.println(staticDisplayTimeNext);
  }
  
  if (oscilloscopeMode == 'a') {
    uint32_t groupCount = oscilloscopeAveragedGroupCount;
    for (uint32_t groupID = 0; groupID < groupCount; ++groupID) {
      float minimum = oscilloscopeCopiedSamples[groupID * 3 + 0];
      float average = oscilloscopeCopiedSamples[groupID * 3 + 1];
      float maximum = oscilloscopeCopiedSamples[groupID * 3 + 2];

      Serial.print(">min:");
      Serial.println(minimum, 4);

      Serial.print(">avg:");
      Serial.println(average, 4);
      
      Serial.print(">max:");
      Serial.println(maximum, 4);
    }
  }
}

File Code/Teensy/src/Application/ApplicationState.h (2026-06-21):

#pragma once

#include "Util/Offline.h"
#include "Util/Vector/Vector.h"
#include <stdint.h>

struct ApplicationState {
  static constexpr bool emulateCurrent = Offline::isOffline;

  uint32_t modeStartIterationID = 0;

  float current = 0; // units: A
  float filteredCurrent = 0; // units: A

  float capacitance = 0; // units: F
  float phaseShift = 0; // units: °
  float dC_dstep = 0; // units: F
  uint32_t capacitanceUpdateCount = 0;

  float spectroscopyTrigger = 0;

  float biasVoltage = 0; // units: V
  float piezoXVoltage = 0; // units: V
  float piezoYVoltage = 0; // units: V
  float piezoZVoltage = 0; // units: V

  float4 abbreviated() const {
    float4 output;
    output.x = piezoXVoltage;
    output.y = piezoYVoltage;
    output.z = piezoZVoltage;
    output.w = filteredCurrent;
    return output;
  }
  float4 previous = float4(0);

private:
  // Delay line for 10 loop iterations.
  float currentSpike[10] = { 
    0, 0, 0, 0, 0,
    0, 0, 0, 0, 0,
  };
  float filteredCurrentSpike = 0;
  float currentMaximum = 0;

  void updateCurrentSpike();

public:
  void updateCurrent(bool useADC);

  void addSpike(float dV, float C);

  float getPredictedCurrentSpike() const;

  // Retrieves the current maximum for usage in logging and resets it.
  float extractCurrentMaximum();

  uint32_t getTimeSinceModeStart();
};

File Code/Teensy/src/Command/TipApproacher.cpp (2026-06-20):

#include "TipApproacher.h"

#include "Application/Application.h"
#include "Filter/Feedback.h"
#include "Time/KilohertzLoop.h"
#include <Arduino.h>

TipApproacher::TipApproacher() {

}

TipApproacher::TipApproacher(TipApproacher::State startingState, bool didContact) {
  currentState = startingState;
  this->didContact = didContact;
  stateStartIterationID = KilohertzLoop::iterationID;
}

TipApproacher::State TipApproacher::rangeRestorationState() {
  float voltageZ = Application::state.piezoZVoltage;

  if (voltageZ >= 250) {
    return State::stepUp;
  } else if (voltageZ <= -60) {
    return State::stepDown;
  } else {
    return State::feedback;
  }
}

bool TipApproacher::modeShouldChange() {
  if (!forceModeChanges) {
    return false;
  }
  
  uint8_t currentMode = uint8_t(Application::mode);
  uint8_t thresholdMode = uint8_t(Command::Mode::idleFeedback);
  if (currentMode < thresholdMode) {
    return false;
  }

  if (rangeRestorationState() != State::feedback) {
    return true;
  } else {
    return false;
  }
}

void TipApproacher::update() {
  updateState();

  Application::setBiasForFeedback();

  float voltageZ = getPiezoVoltage();
  if (voltageZ == -1000) {
    Application::correctZVoltage();
  } else {
    Application::updatePiezoVoltage(3, voltageZ);
  }
}

uint32_t TipApproacher::getIterationsSinceStateStart() {
  uint32_t deltaIters = KilohertzLoop::iterationID;
  deltaIters -= stateStartIterationID;
  return deltaIters;
}

void TipApproacher::updateState() {
  State previousState = currentState;

  uint32_t deltaIters = getIterationsSinceStateStart();
  uint32_t time = deltaIters * KilohertzLoop::period;

  switch (previousState) {
    case State::waitBeforeApproach: {
      if (time >= 1250) {
        currentState = State::approach;
      }
      break;
    }
    case State::approach: {
      if (Application::state.piezoZVoltage >= 270) {
        currentState = State::stepUp;
      } else {
        float current = Application::state.current;
        float setpoint = Feedback::setpointCurrent;
        if (abs(current) >= setpoint) {
          currentState = State::feedback;
          didContact = true;
        }
      }
      break;
    }
    case State::stepUp: {
      if (time >= 800) {
        currentState = State::waitBeforeApproach;
      }
      break;
    }
    case State::stepDown: {
      if (time >= 1600) {
        currentState = State::approach;
      }
      break;
    }
    case State::feedback: {
      break;
    }
  }

  if (currentState == State::feedback) {
    currentState = rangeRestorationState();
  }

  if (currentState != previousState) {
    stateStartIterationID = KilohertzLoop::iterationID;
  }
}

float TipApproacher::getPiezoVoltage() {
  uint32_t deltaIters = getIterationsSinceStateStart();
  float voltageZ = Application::state.piezoZVoltage;

  switch (currentState) {
    case State::waitBeforeApproach: {
      float dV = 1.4 * float(KilohertzLoop::period);
      if (voltageZ < -80) {
        return min(voltageZ + dV, -80);
      } else if (voltageZ > -80) {
        return max(voltageZ - dV, -80);
      } else {
        return -80;
      }
    }
    case State::approach: {
      // Retracting at 840 V / 600 μs
      // Δx_equilibrium reaches -5.4 nm in 12 μs
      // acceleration reaches -0.46 m/s^2 at 1.47 kHz resonance
      // 1000 nm/s velocity comes to a stop in 2.2 μs
      float speed = float(50e-12) / float(64e-6 + 20e-6 + 2.2e-6);
      
      float dVdt = speed / float(0.320e-9);
      float dt = float(KilohertzLoop::period) * 1e-6;
      return min(voltageZ + dVdt * dt, 270);
    }
    case State::stepUp: {
      float startVoltage = (didContact ? 20 : 80);

      if (voltageZ > startVoltage) {
        float dV = 1.4 * float(KilohertzLoop::period);
        return max(voltageZ - dV, startVoltage);
      } else {
        return -270;
      }
    }
    case State::stepDown: {
      uint32_t time = deltaIters * KilohertzLoop::period;
      if (time < 600) {
        float dV = 1.4 * float(KilohertzLoop::period);
        return max(voltageZ - dV, -270);
      } else {
        return -80;
      }
    }
    case State::feedback: {
      if (deltaIters < 4) {
        return max(voltageZ - 15, -80);
      } else {
        return -1000;
      }
    }
  }

  Serial.println("This should never happen.");
  exit(0);
}

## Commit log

2026-01-16 Prepare settings for KiCad projects
    [HighVoltageBoard.kicad_pcb, HighVoltageBoard.kicad_sch, MainBoard.kicad_pcb, MainBoard.kicad_sch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]
2026-01-16 Added PA95 footprint draft
    [MainBoard.kicad_pcb, MainBoard.kicad_sch]
2026-01-16 Remove old PA95 footprint from board
    [MainBoard.kicad_pcb]
2026-01-20 Model of lab space
    [LabSpace.FCStd]
2026-01-20 Add silicone mat model
    [LabSpace.FCStd]
2026-01-20 Save progress
    [LabSpace.FCStd]
2026-01-22 Attempt to not add .FCBak
    [LabSpace.FCStd]
2026-01-23 Viton damper not needed or helpful
    [LabSpace.FCStd]
2026-01-24 Updated the FreeCAD model
    [LabSpace.FCStd]
2026-02-04 Finished the isolators
    [Isolation.kicad_sch]
2026-02-05 Finished the DACs
    [DAC1.kicad_sch, DAC2.kicad_sch, Isolation.kicad_sch]
2026-02-05 Finished the sensors
    [ADC.kicad_sch, Amplifier.kicad_sch, CDC.kicad_sch, DAC2.kicad_sch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]
2026-02-05 Save progres
    [15V.kicad_sch, Amplifier.kicad_sch, Converter.kicad_sch, PreAmp.kicad_sch]
2026-02-05 Finished with the chips for the transimpedance amplifiers
    [Amplifier.kicad_sch, CompensationNetwork.kicad_sch, TIA1.kicad_sch, TIA2_Post.kicad_sch]
2026-02-16 Added practice board project
    [PracticeBoard.kicad_pcb, PracticeBoard.kicad_sch]
2026-02-16 Change universal THT receptacle to pin socket
    [HighVoltageBoard.kicad_sch]
2026-02-17 Added mounting holes
    [HighVoltageBoard.kicad_sch, MainBoard.kicad_sch, PowerBoard.kicad_sch]
2026-02-18 Connectors should be fully specified now
    [ADC.kicad_sch, Amplifier.kicad_sch, DAC1.kicad_sch, HighVoltageBoard.kicad_sch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]
2026-02-18 Updated exclude from BOMs
    [ADC.kicad_sch, Amplifier.kicad_sch]
2026-02-18 Preparing to revert this change to the footprints
    [MainBoard.kicad_pcb]
2026-02-18 Footprint change has been reverted
    [MainBoard.kicad_pcb]
2026-02-18 Should be at a major turning point in the project
    [Isolation.kicad_sch, MainBoard.kicad_sch, Teensy.kicad_sch]
2026-02-18 Passes ERC
    [15V.kicad_sch, ADC.kicad_sch, Amplifier.kicad_sch, CDC.kicad_sch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]
2026-02-19 Should be finished with components BOM
    [15V.kicad_sch, ADC.kicad_sch, Amplifier.kicad_sch, CDC.kicad_sch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]
2026-02-19 The two resistors have been revised
2026-02-20 Finished THT footprints
    [HighVoltageBoard.kicad_pcb]
2026-02-20 Finished designing the footprints
    [HighVoltageBoard.kicad_pcb]
2026-02-20 Assigned footprints
    [15V.kicad_sch, ADC.kicad_sch, Amplifier.kicad_sch, CDC.kicad_sch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]
2026-02-20 Starting layout of the high voltage board
    [Amplifier.kicad_sch, HighVoltageBoard.kicad_pcb]
2026-02-20 This is not an acceptable connector packing arrangement
    [MainBoard.kicad_pcb]
2026-02-23 Push uncommitted changes
    [HighVoltageBoard.kicad_pcb, MainBoard.kicad_pcb, PowerBoard.kicad_pcb, TIA1.kicad_pcb]
2026-02-23 Everything is now aligned very well on the power board
    [15V.kicad_sch, Converter.kicad_sch, MainBoard.kicad_pcb, MainBoard.kicad_sch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]
2026-02-23 Better dowel pin alignment
    [PowerBoard.kicad_pcb]
2026-02-24 Finished layout of power board
    [HighVoltageBoard.kicad_pcb, PowerBoard.kicad_pcb, WallPower.kicad_sch]
2026-02-25 Aligned all of the parts near the PA95 op amps
    [Amplifier.kicad_sch, HighVoltageBoard.kicad_pcb, HighVoltageBoard.kicad_sch, MainBoard.kicad_pcb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]
2026-02-25 I am overcomplicating the TIA1 board
    [ADC.kicad_sch, CDC.kicad_sch, DAC1.kicad_sch, DAC2.kicad_sch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]
2026-02-26 Weird bug messes up FEM simulation results when I recompute objects in FreeCAD
    [Resistor_0805_Mounted.FCStd, TIA2_Pre.kicad_sch]
2026-02-26 Designing the new FreeCAD model for different dimensions is a pointless waste of time, cut my losses
    [Resistor_0805_Mounted.FCStd]
2026-02-26 ERC passes for the two new boards
    [Amplifier.kicad_sch, CompensationNetwork.kicad_sch, Limiter.kicad_sch, PracticeBoard.kicad_pcb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]
2026-02-26 First time that all PCBs are fully wired
    [CompensationNetwork.kicad_sch, HighVoltageBoard.kicad_pcb, Limiter.kicad_sch, PowerBoard.kicad_pcb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]
2026-03-10 Placed grid origins
    [15V.kicad_sch, HighVoltageBoard.kicad_pcb, MainBoard.kicad_pcb, MainBoard.kicad_sch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]
2026-03-12 Tried everything, Arduino does not even work
2026-03-13 Rename this folder to Teensy
2026-03-16 Preamplifier design is done
    [PreAmp.kicad_pcb, PreAmp.kicad_sch]
2026-03-16 Finished designing the piezos
    [PhaseII.FCStd, PreAmp.kicad_pcb]
2026-03-16 Fixed the PCB
    [PhaseII.FCStd, PreAmp.kicad_pcb, PreAmp.kicad_sch]
2026-03-18 Save images
    [PhaseII.FCStd]
2026-03-20 Designed all of the piezo aligners
    [PhaseII.FCStd]
2026-03-20 Don't know what has changed in FreeCAD
    [PhaseII.FCStd, PreAmp.kicad_pcb]
2026-03-20 Save changes
    [PhaseII.FCStd, PreAmp.gbr, PreAmp.kicad_pcb]
2026-03-22 Final revisions before order
    [CNC.FCStd, PhaseII.FCStd, STM Base.step]
2026-03-25 Filter out kicad lck files
2026-03-25 It's measuring capacitances with the correct magnitude
2026-03-25 The chip is measuring capacitance, let's move on to other goals
2026-03-28 Made the KiCad schematic revision
    [Amplifier.kicad_sch]
2026-03-28 Check how this table formatting works
    [Amplifier.kicad_sch]
2026-03-29 Filmed the video
    [Amplifier.kicad_sch]
2026-03-29 Some additions to the header files
    [Amplifier.kicad_sch]
2026-03-29 Offset problem is fixed, although this investigation did lead to the destruction of one PA95
    [Amplifier.kicad_sch]
2026-04-01 Upload media
    [PhaseI.FCStd]
2026-04-01 Ported over a reduced version of the capacitance measurement loop
2026-04-05 Strange behavior with Teensy acting unpredictable
2026-04-05 Save current state of code
2026-04-05 Just going to hand solder a fresh chip
2026-04-06 Calibrated the new CDC
2026-04-06 Upload image of 3D printed parts
2026-04-17 Code for 420 V sound test
2026-04-24 Calibration is finished
2026-05-11 The code no longer has major issues for streaming serial data from Teensy to PC
2026-05-18 Numerical instability in the biquad filter, fixed it with FP64 for now
2026-05-22 I have an idea to solve the problem where stability is improved from exponentially higher repulsion at high currents
2026-05-25 We need an internal model of response to current spikes
2026-05-26 Capacitance tracking is fixed
2026-06-03 Implemented code for notch filter
2026-06-04 Finished updating the Teensy code
2026-06-04 Save this change to the Teensy code
2026-06-06 Fixed a Teensy bug
2026-06-12 Implemented Sample
2026-06-12 Beautiful refactorings to the Swift prototype of CreepFilter
2026-06-12 Finished implementing Filter
2026-06-12 Program is too slow on the Teensy
2026-06-14 Added creep filter to SerialInterface
2026-06-14 Solved some problems with coding of the line extraction thread
2026-06-19 This might be a solution to a crash in the creep filter
2026-06-20 Finished drafting the Teensy code for now
2026-06-21 Improvements to capacitance tracker
2026-06-22 Save calibration data for 8i,20,20,1
